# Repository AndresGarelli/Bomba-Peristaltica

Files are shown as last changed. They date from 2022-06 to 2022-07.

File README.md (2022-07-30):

English version (Spanish version at the end) updated 2022-07-30

Peristaltic pump

The Arduino code is based on https://www.thingiverse.com/thing:2619479/files and modified to meet my needs, especially related to calibration. 
We do not need to fill the vials with an exact volume, so I designed a “by eye” calibration method.

Two critical points to consider:
-	Use PETG to print rotor pieces. It resists quite well up to 85ºC. On the other hand, PLA, the most frequently used material for 3D printing softens at 65C. The rest of the pieces were printed with PLA and work fine, at least for the moment.
-	Food temperature: We cook the fly food at 95ºC for 30 minutes. That high temperature softens PLA, and probably PETG. We now cook the food at 95 and let it cool (and maintain it at) 75ºC to deliver into the vials. It is very important to keep food at a constant temperature to deliver a reproducible volume. Food viscosity increases when temperate decreases and if the pump has been calibrated at a high temperature to deliver a given volume in a given number of rotations, then the volume delivered by the same number of rotations will be smaller when the food cools down.

The design of the rotor is a modification of https://www.thingiverse.com/thing:3148717. I followed the designer recommendation to print with 100% infill. Remember to use PETG, at least for the rotor.

Two different calibration values can be saved in the programs named “moscas” (flies) and “gusanos” (worms). If necessary, those names can be changed in lines 161 and 162 of the code.

The pressure of the cover over the hose is adjusted with two long screws. If the cover is too loose, the rotor will not make enough pressure onto the hose and the food will not be pumped. If it is too tight, it will block the motor. The exact position should be found by trial and error. If you find that my design does not work in your hands, you can try with the original one https://www.thingiverse.com/thing:3148717.

A few comments on the electronic circuit. There are three things that are optional and can be removed. The first one is the possibility to activate the pump with a pedal. We found that it was not necessary after adding the option to repeat pumping cycles to the code. The second one are the three LEDs that indicate the mode of operation that is selected. The same information is shown in the screen. The last one is the fan to cool the motor and the motor driver. It does not seem necessary since none of them gets too hot during operation.

Bill of Materials (with links to suppliers in Argentina)

1- Stepper motor, 1.5A high Torque 4.2kg 17HS4401S   x1 https://articulo.mercadolibre.com.ar/MLA-899670687-nema-17-motor-paso-a-paso-18-alto-t-15a-usongshine-_JM

2- Bearings  605zz	x9	https://articulo.mercadolibre.com.ar/MLA-915854069-rodamiento-ruleman-605-zz-x20-unidades-_JM

3- driver A4899		x1 https://www.todomicro.com.ar/motores-y-drivers-motores/288-modulo-a4988-pololu-driver-motor-paso-a-paso.html

4- arduino promini 5V (it will also work with proMini 3.3V or arduino UNO)	x1

5- Power source 12V 2A		x1

6- step down regulator MP1584 	x1

7- 16x2 LCD display with I2C adapter	x1

8- Rotary encoder Ky-040 	x1

9- LEDs 3mm (optional)	x3

10-  100uF capacitor	x1

11- resistors 220 Ohm, 10kOhm

12- Fan, 6cm (optional)	x1

13- Plastic box: it can be printed, I used a 20x30 cm for electrical installations

14- silicone hose, external diameter 10mm, inner diameter 6mm (walls 2mm). 

15- nuts, bolts, screws, etc

It is critical to limit the current through the motor driver!

This is VERY important. If this is not correctly done the motor can be damaged. For a detailed explanation, visit this webpage: https://www.pololu.com/product/1182
I used a cheap driver that does not have the same resistor values as the original one. This has to be taken into account when setting the current limit.  I provide the details of the procedure for my motor and driver, you should do your own calculations:

Motor 17HS4401S

Max current 1.5A

For a A4988 driver:  Imax = Vref/8*limiting resistor.

Imax is 1.5

Resistor: R100 0.1Ohm or 100 mOhm

Vref= 1.2V

The driver is configured to work in a quarter steps  mode with a logic level of 5V.
Turn the potentiometer of the driver until you get the Vref. In my case, I had to put the potentiometer at the max max level to get a  Vref of 1.19V.

User instructions:

The LCD display shows a menu with 11 options that can be navigated turning the knob clockwise or counterclockwise. Menu options are selected by pressing the knob once. Once inside the option, turn the knob to set values and press again to leave.
If the knob is pressed continuously the motor will move at a constant speed until the knob is released. That will let the operator fill the hose with food.
The pumb has three operation modes: Dosifica (dosing), bombea (pump), calibra (calibration).

MENU OPTIONS 

0: Start--> starts the selected mode (dosifica/bombea/calibra). Pressing a second time stops the pump once the current cycle is finished.

1: Tiempo (time)--> Sets the time required to fill one vial. When this value is set, the speed expressed as RPM is automatically calculated. If the resulting speed is > 200 RPM, the time is decreased to get a max speed of 200 RPM.

2: Velocidad (speed)--> Sets the speed, expressed in RPM, and calculates the time required to fill one vial.

3: Ciclos (cycles) --> Number of filling cycles that will be executed when pressing START (number of vials to fill). Max value is 200. This value can be increased in line 139 of the code.

4: Pausa (pause) --> Resting time between two consecutive cycles.

5: Modo (mode)--> It has three options. Dosifica (= dosing. The motor will move a given number of turns defined during the calibration and stop for the time established in menú 5. The cycle is repeated the number of times indicated in menú 4). Bombea (=pump. The motor turns at a constant speed) and Calibra (=calibration. The pump executes a calibration cycle and returns to the dosing mode)

6: PGM --> Used to store two different dispensing volumes (ie two different calibration values)

7: Sentido (turning direction)--> H (Horario: clockwise) and AH (AntiHorario: counter clockwise)

8:  M--> is the number of steps that the motor will move in the program “Moscas” (200 steps is one turn. In fact, as the driver is set at quarter steps, 800 steps are required to move the motor one turn. The number set in this menu is internally multiplied by 4). 

9: G--> Same as above, but for the program Gusanos. Both 9 and 10 can be manually set, and the speed will be automatically calculated to complete the cycle in the time indicated in menu 2 (time). 

10: Saves the configuration in the memory of the Arduino board. The values of each parameter are loaded from memory at start. After calibration (or changing speed, cycles, puase time, etc) the new settings can be saved by selecting this option. 

How to use the pump?

Place the silicone hose between the rotor and hose cover and tighten the cover with the screws until an optimal position is reached. An optimal position is that at which the bearings are tightly adjusted to hose and the motor is not blocked. (https://youtu.be/28UxOIC15p4)

Calibration

Select the program to calibrate in menú 7 (Moscas or gusanos. Or, for example, big and small vial)
Select the option “calibrar” in menú 6. The LCD will show the message “Presionar hasta llenar el tubo” (press until the vial is filled).
Place the end of the hose inside one empty vial and keep the knob pressed. The motor will begin to move slowly and pump the food. Release the knob when the desired level of food is reached. The program will save the number of turns and calculate how long it will take to fill one vial (menu 2) at the speed set in menu 3. The number of turns and steps will be diplayed for a few seconds and will automatically change to the dosing mode.

Pumping

Go to menú 1 and press the knob. The motor will move and the Word RUN will be displayed in the screen. 
If the mode “bombea” is selected, the motor will rotate until the knob is pressed again.
If it is in mode “Dosifica”, the motor will move for one cycle, make a pause and repeat the process as many times as indicated by menu4. Press the knob to stop dosing. Remember that the motor will stop once the current cycle has finished.

Versión en castellano

Bomba peristáltica

El código del arduino está basado en https://www.thingiverse.com/thing:2619479/files  y modificado según mis necesidades, en particular, la forma de calibración. Nosotros no necesitamos un volumen exacto y además la consistencia de la comida varía bastante en función de la temperatura, por lo que el ajuste para que dispense un cierto volumen puede cambiar bastante en función de la temperatura de la comida. Por eso implementé un calibrado “a ojo” que es más que suficiente para mis necesidades.

Hay dos puntos críticos a tener en cuenta:
-material utilizado para imprimir las piezas: el PLA se ablanda a 65ºC aproximadamente. Las primeras pruebas fueron impresas con ese material y no funcionaron bien, en particular, el rotor. Por eso rediseñé el rotor y lo imprimí en PETG, que resiste bien hasta 85C. El resto de las piezas no fueron reimpresas en ese material. Aparentemente, funcionan bien en PLA.
-temperatura de la comida: cocinamos la comida en una olla a baño maría con termostato fijo a 95C. A esa temperatura, el PLA se ablanda. El rotor es particularmente sensible a este efecto porque se deforma el orificio donde encaja el motor. Por eso, lo reimprimimos con PETG y además bajamos la temperatura a 70C para distribuirla. Es decir, cocinamos a 95 y luego bajamos a 70C. De esa manera, logramos distribuir 4 litros de comida sin ningún inconveniente. Por otra parte, es importante que se mantenga la temperatura de la comida ya que si se calibra a una temperatura para que impulse un cierto volumen de comida en cada ciclo y luego la comida se enfría, el volumen dispensado va a ser menor. La solución es recalibrar (es muy fácil de hacer) cuando sea necesario o mantener la comida a una temperatura fija.

El modelo inicial del rotor fue copiado de https://www.thingiverse.com/thing:3148717 pero luego modificado y es el que se adjunta. Recomienda imprimirlo con infill 100%. Yo recomiendo usar PETG, al menos para el rotor.

Mi idea era hacer una bomba que pudiera usarse por dos laboratorios diferentes, el mío, que trabaja con moscas y otro de gusanos (por eso tiene dos programas denominados “moscas” y “gusanos”. Se puede cambiar el nombre en las líneas 161 y 162 del código). En este último caso, se necesita distribuir un medio de cultivo estéril y por lo tanto, necesitan esterilizar la manguera luego de cada uso. Para que fuera sencillo cambiar la manguera luego de cada uso diseñé las piezas que adjunto. Pero luego no funcionaron tal como esperaba, ya que para evitar que el motor se trabe es necesario que las piezas tengan algo de juego, que puedan moverse levemente. La solución que encontré fue hacerles un agujero con un taladro y atravesar un tornillo para mantener unidas las dos piezas entre sí y dejar que puedan moverse. Los orificios ya están incluidos en el modelo adjunto. Este diseño se parece bastante en su funcionamiento a aquel del que copié el rotor. La manguera puede aun cambiarse con relativa facilidad. Si sólo vas a ser usado para comida de moscas, quizás pueda ser más práctico imprimir directamente el modelo completo del que saqué el rotor, que también incluye una carcasa para alojar el motor y el controlador. El cambio de la manguera parece más trabajoso en ese modelo, pero eso no sería un inconveniente si no es necesario esterilizarla luego de cada uso ya que puede lavarse el interior pasando agua caliente.
Acerca del circuito eléctrico. Hay tres cosas que son opcionales. Una es la activación con un pedal. La idea era llenar los tubos de a uno activando la bomba con un pedal, pero encontramos que la alternativa de generar un programa con un número de ciclos (=tubos) y una pausa entre ellos era mejor. La otra característica opcional son los leds que indican el modo de funcionamiento. La última es el ventilador para enfriar el driver del motor y el motor mismo. Las especificaciones del driver indican que puede llegar a ser necesario refrigerarlo. Como es barato, preferí agregarlo, pero me parece que funcionaría igual de bien sin él.
 
Lista de materials con links a proveedores en Argentina
1- motor paso a paso (stepper motor) 1.5A Alto Torque 4.2kg 17HS4401S   x1 https://articulo.mercadolibre.com.ar/MLA-899670687-nema-17-motor-paso-a-paso-18-alto-t-15a-usongshine-_JM

2- ruleman 605zz	x9	https://articulo.mercadolibre.com.ar/MLA-915854069-rodamiento-ruleman-605-zz-x20-unidades-_JM
3- driver A4899		x1 https://www.todomicro.com.ar/motores-y-drivers-motores/288-modulo-a4988-pololu-driver-motor-paso-a-paso.html

4- arduino promini 5V (se puede usar también de 3.3V o un arduino UNO)	x1

5- Fuente 12V 2A	x1

6- Regulador step down MP1584 	x1

7- Display LCD 16x2 con adaptador I2C	x1

8- Encoder Rotativo Ky-040 	x1

9- LEDs 3mm (opcional)	x3

10- condensador de 100uF	x1

11- resistencias 220 Ohm, 10kOhm

12- ventilador de 6cm (opcional)	x1

13- caja plástica: se puede imprimir. Usé una caja estanca de aprox 20x30 cm

14- la manguera es de silicona diámetro ext 10mm, diámetro int 6mm (paredes 2mm). 

15- tornillos, tuercas…

AJUSTES de corriente máxima para el driver del motor

Este punto es muy importante. Hay que seguir las instrucciones que se encuentran aquí: https://www.pololu.com/product/1182
El módulo que conseguí no es el original y no tiene las resistencias que se indican en ese instructivo. De todas maneras, el método de ajuste es el mismo. A continuación, pego mis notas respecto de esto:

Motor 17HS4401S										intensidad máxima es 1.5A	

para ajustar el A4988 Imax = Vref/8*resistencia limitadora

Imax es 1.5      la resistencia es R100 0.1Ohm o 100 mOhm

Vref= 1.2V

Uso el driver en modo quarter steps con un nivel lógico de 5V.

Ajustando el potenciómetro del módulo al máximo, el máximo valor Vref alcanzado es de 1.19V, que es el Vref con el que se alcanza el Imax de 1.5 A
es decir, que quedó en el límite superior.

Funcionamiento:

Al encenderla, aparece en el display un menú con 11 opciones. Girando el control en sentido horario o antihorario se cambia de menú. Presionando la misma perilla, se entra en el menú y pueden seleccionarse opciones. Presionando nuevamente, se sale del menú.
En cualquier momento, si se mantiene presionado el selector comenzará a funcionar la bomba a una velocidad fija (no necesariamente la misma que la seleccionada en el menú 3) en forma continua hasta que se suelte. Eso permite llenar la manguera.

MENU

0: Start--> inicia el programa (dosifica/bombea/calibra). Presionando nuevamente, interrumpe la ejecución al finalizar el ciclo actual.

1: Tiempo --> permite establecer el tiempo de llenado deseado. Calcula automáticamente las RPM. Si RPM es mayor que 200, ajusta el tiempo para no sobrepasar 200.

2: Velocidad --> permite ajustar RPM, calcula automáticamente el tiempo de llenado.

3: Ciclos --> número de ciclos a repetir al presionar start. (es decir, número de tubos a llenar). Máximo 200. Se puede aumentar en la línea 139 del programa.

4: Pausa --> tiempo de espera entre dos ciclos. Permite posicionar la manguera sobre un nuevo tubo vacío

5: Modo --> Tiene tres opciones. Dosifica (ejecuta un ciclo durante el que gira el número de veces seleccionado durante la calibración y luego frena. Hace una pausa y vuelve a arrancar hasta completar el número de ciclos indicados en el menú 4). Bombea (el motor gira a la velocidad seleccionada en menú 3) y Calibra (ejecuta un ciclo de calibración y luego vuelva automáticamente a modo Dosifica)

6: PGM --> permite almacenar dos volumenes diferentes para dispensar comida

7: Sentido --> sentido de giro

8:  M--> es el número de pasos que da el motor en el programa moscas (200 pasos es una vuelta). 

9: G--> es el número de pasos que da el motor en el programa gusanos (200 pasos es una vuelta). 

10: Guarda configuración en memoria: Al iniciar el programa carga valores por defecto en la memoria. Luego de calibrar (o modificar la velocidad, ciclos, pausa) se debe ejecutar esta opción del menú para que se guarden en la memoria. En caso contrario, la vez siguiente que se encienda el equipo volverá a los valores por defecto.

Inicio

Ajustar la posición del cubrerotor para que los rulemanes ajusten perfectamente bien la manguera, pero que no bloqueen el motor. La manguera está bien ajustada cuando al soplar por un extremo no es posible hacer circular aire. (https://youtu.be/28UxOIC15p4)

Calibración

Seleccionar en el menú 7 un programa para calibrar (moscas o gusanos. O tubo grande/chico).
En menú 6 seleccionar la opción calibrar. Aparece un mensaje que dice: “Presionar hasta llenar el tubo”
Posicionar la manguera sobre un tubo vacío y mantener presionado el botón. El motor comenzará a girar lentamente. Soltar el botón cuando se alcance el nivel de comida deseado. El programa almacena el número de vueltas dado y calcula cuánto tiempo demorará en llenar el tubo (nuevo valor del menú 2) en función de la velocidad indicada en el menú 3. Luego muestra el  número de pasos y el número de vueltas del motor. Al finalizar la rutina pasa al modo dosifica automáticamente.

Dosificación

Girar la perilla hasta llegar al menú 1 y presionar el botón. Aparece la leyenda RUN. Según el modo, bombea, dosifica o calibra.
Si está en modo “Dosifica”, arranca el motor, cumple un ciclo y hace una pausa (de duración establecida en menú 5). Repite el proceso tantas veces como se haya indicado en el menú 4
La ejecución de la serie de ciclos se puede interrumpir presionando nuevamente la perilla. El efecto no es inmediato, primero tiene que terminar de ejecutar el ciclo actual y luego frena.

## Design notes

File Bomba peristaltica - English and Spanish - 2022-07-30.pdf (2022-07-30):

English version (Spanish version at the end) updated: 2022-07-30

## Peristaltic pump

The Arduino code is based on https://www.thingiverse.com/thing:2619479/files and modified to meet my needs, especially related to calibration. We do not need to fill the vials with an exact volume, so I designed a “by eye” calibration method.

Two critical points to consider:

- Use PETG to print rotor pieces. It resists quite well up to 85ºC. On the other hand, PLA, the most frequently used material for 3D printing softens at 65C. The rest of the pieces were printed with PLA and work fine, at least for the moment.
- Food temperature: We cook the fly food at 95ºC for 30 minutes. That high temperature softens PLA, and probably PETG. We now cook the food at 95 and let it cool (and maintain it at) 75ºC to deliver into the vials. It is very important to keep food at a constant temperature to deliver a reproducible volume. Food viscosity increases when temperate decreases and if the pump has been calibrated at a high temperature to deliver a given volume in a given number of rotations, then the volume delivered by the same number of rotations will be smaller when the food cools down.

The design of the rotor is a modification of https://www.thingiverse.com/thing:3148717. I followed the designer recommendation to print with 100% infill. Remember to use PETG, at least for the rotor.

Two different calibration values can be saved in the programs named “moscas” (flies) and “gusanos” (worms). If necessary, those names can be changed in lines 161 and 162 of the code.

The pressure of the cover over the hose is adjusted with two long screws. If the cover is too loose, the rotor will not make enough pressure onto the hose and the food will not be pumped. If it is too tight, it will block the motor. The exact position should be found by trial and error. If you find that my design does not work in your hands, you can try with the original one https://www.thingiverse.com/thing:3148717.

A few comments on the electronic circuit. There are three things that are optional and can be removed. The first one is the possibility to activate the pump with a pedal. We found that it was not necessary after adding the option to repeat pumping cycles to the code. The second one are the three LEDs that indicate the mode of operation that is selected. The same information is shown in the screen. The last one is the fan to cool the motor and the motor driver. It does not seem necessary since none of them gets too hot during operation.

Bill of Materials (with links to suppliers in Argentina)

1- Stepper motor, 1.5A high Torque 4.2kg 17HS4401S x1 https://articulo.mercadolibre.com.ar/MLA-899670687-nema-17-

motor-paso-a-paso-18-alto-t-15a-usongshine-_JM (https://articulo.mercadolibre.com.ar/MLA-899670687-nema-17-motor-paso-a-paso-18-alto-t-15a-usongshine-_JM)
2- | Bearings 605zz x9 | https://articulo.mercadolibre.com.ar/MLA-915854069-rodamiento-ruleman-605-zz-x20-
unidades-_JM (https://articulo.mercadolibre.com.ar/MLA-915854069-rodamiento-ruleman-605-zz-x20-unidades-_JM)
3- driver A4899 x1 https://www.todomicro.com.ar/motores-y-drivers-motores/288-modulo-a4988-pololu-driver-motor-paso-apaso.html (https://www.todomicro.com.ar/motores-y-drivers-motores/288-modulo-a4988-pololu-driver-motor-paso-a-paso.html)
4- arduino promini 5V (it will also work with proMini 3.3V or arduino UNO) x1
5- | Power source 12V 2A x1
6- | step down regulator MP1584 x1
7- | 16x2 LCD display with I2C adapter x1
8- | Rotary encoder Ky-040 x1
9- | LEDs 3mm (optional) x3

10- 100uF capacitor x1
11- resistors 220 Ohm, 10kOhm
12- Fan, 6cm (optional) x1
13- Plastic box: it can be printed, I used a 20x30 cm for electrical installations 14- silicone hose, external diameter 10mm, inner diameter 6mm (walls 2mm). 15- 15- nuts, bolts, screws, etc

It is critical to limit the current through the motor driver!

This is VERY important. If this is not correctly done the motor can be damaged. For a detailed explanation, visit this webpage: https://www.pololu.com/product/1182 I used a cheap driver that does not have the same resistor values as the original one. This has to be taken into account when setting the current limit. I provide the details of the procedure for my motor and driver, you should do your own calculations:

Motor 17HS4401S
Max current 1.5A
For a A4988 driver: Imax = Vref/8*limiting resistor. Imax is 1.5
Resistor: R100 0.1Ohm or 100 mOhm
Vref= 1.2V

The driver is configured to work in a quarter steps mode with a logic level of 5V. Turn the potentiometer of the driver until you get the Vref. In my case, I had to put the potentiometer at the max max level to get a Vref of 1.19V.

User instructions: The LCD display shows a menu with 11 options that can be navigated turning the knob clockwise or counterclockwise. Menu options are selected by pressing the knob once. Once inside the option, turn the knob to set values and press again to leave. If the knob is pressed continuously the motor will move at a constant speed until the knob is released. That will let the operator fill the hose with food. The pumb has three operation modes: Dosifica (dosing), bombea (pump), calibra (calibration).

Menu 0: Start--> starts the selected mode (dosifica/bombea/calibra). Pressing a second time stops the pump once the current cycle is finished.

Menu 1: Tiempo (time)--> Sets the time required to fill one vial. When this value is set, the speed expressed as RPM is automatically calculated. If the resulting speed is > 200 RPM, the time is decreased to get a max speed of 200 RPM.

Menu 2: Velocidad (speed)--> Sets the speed, expressed in RPM, and calculates the time required to fill one vial.

Menu 3: Ciclos (cycles) --> Number of filling cycles that will be executed when pressing START (number of vials to fill). Max value is 200. This value can be increased in line 139 of the code.

Menu 4: Pausa (pause) --> Resting time between two consecutive cycles.

Menu 5: Modo (mode)--> It has three options. Dosifica (= dosing. The motor will move a given number of turns defined during the calibration and stop for the time established in menú 5. The cycle is repeated the number of times indicated in menú 4). Bombea (=pump. The motor turns at a constant speed) and Calibra (=calibration. The pump executes a calibration cycle and returns to the dosing mode)

Menu 6: PGM --> Used to store two different dispensing volumes (ie two different calibration values)

Menu 7: Sentido (turning direction)--> H (Horario: clockwise) and AH (AntiHorario: counter clockwise)

Menu 8: M--> is the number of steps that the motor will move in the program “Moscas” (200 steps is one turn. In fact, as the driver is set at quarter steps, 800 steps are required to move the motor one turn. The number set in this menu is internally multiplied by 4).

Menu 9: G--> Same as above, but for the program Gusanos. Both 9 and 10 can be manually set, and the speed will be automatically calculated to complete the cycle in the time indicated in menu 2 (time).

Menu 10: Saves the configuration in the memory of the Arduino board. The values of each parameter are loaded from memory at start. After calibration (or changing speed, cycles, puase time, etc) the new settings can be saved by selecting this option.

How to use the pump?

Place the silicone hose between the rotor and hose cover and tighten the cover with the screws until an optimal position is reached. An optimal position is that at which the bearings are tightly adjusted to hose and the motor is not blocked. (https://youtu.be/28UxOIC15p4)

Calibration

Select the program to calibrate in menú 7 (Moscas or gusanos. Or, for example, big and small vial) Select the option “calibrar” in menú 6. The LCD will show the message “Presionar hasta llenar el tubo” (press until the vial is filled). Place the end of the hose inside one empty vial and keep the knob pressed. The motor will begin to move slowly and pump the food. Release the knob when the desired level of food is reached. The program will save the number of turns and calculate how long it will take to fill one vial (menu 2) at the speed set in menu 3. The number of turns and steps will be diplayed for a few seconds and will automatically change to the dosing mode.

Pumping

Go to menú 1 and press the knob. The motor will move and the Word RUN will be displayed in the screen. If the mode “bombea” is selected, the motor will rotate until the knob is pressed again. If it is in mode “Dosifica”, the motor will move for one cycle, make a pause and repeat the process as many times as indicated by menu4. Press the knob to stop dosing. Remember that the motor will stop once the current cycle has finished.

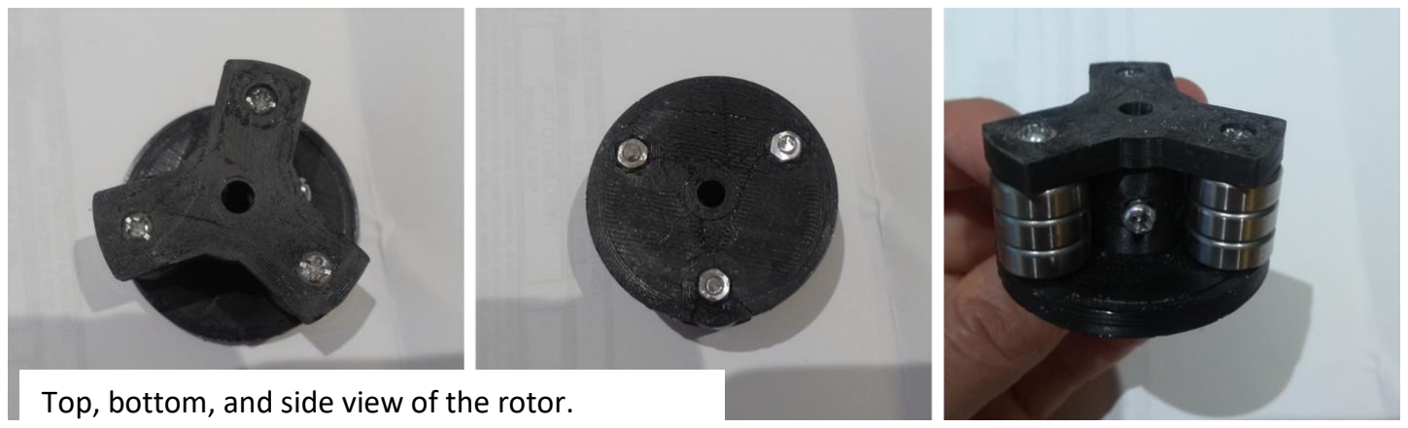
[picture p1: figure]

Top, bottom, and side view of the rotor.

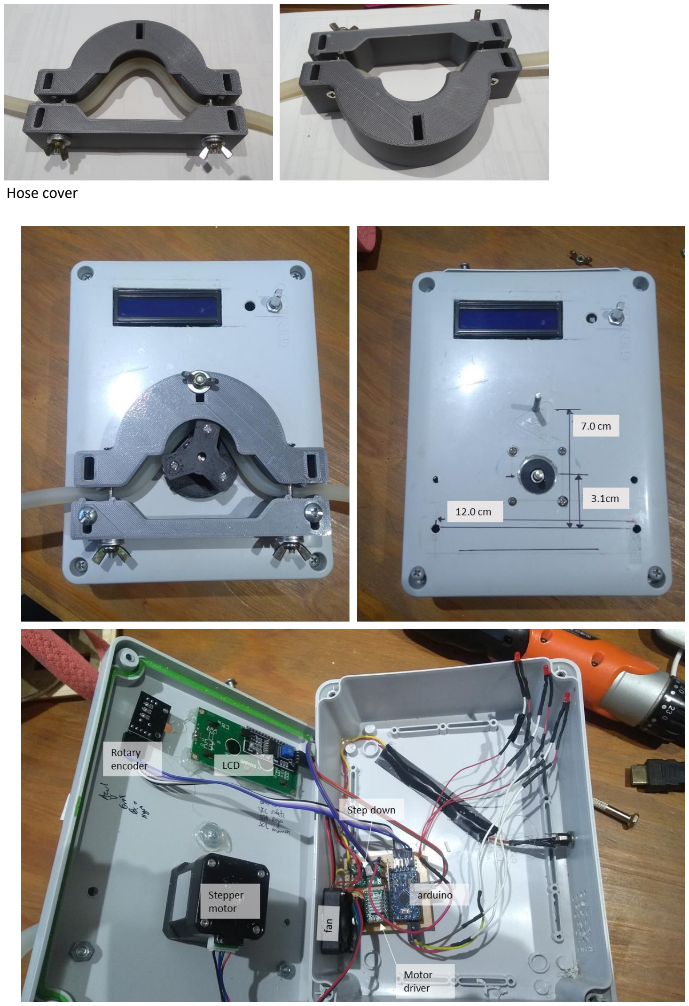
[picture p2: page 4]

Hose cover

## Versión en castellano

## Bomba peristáltica

El código del arduino está basado en https://www.thingiverse.com/thing:2619479/files y modificado según mis necesidades, en particular, la forma de calibración. Nosotros no necesitamos un volumen exacto y además la consistencia de la comida varía bastante en función de la temperatura, por lo que el ajuste para que dispense un cierto volumen puede cambiar bastante en función de la temperatura de la comida. Por eso implementé un calibrado “a ojo” que es más que suficiente para mis necesidades.

Hay dos puntos críticos a tener en cuenta: -material utilizado para imprimir las piezas: el PLA se ablanda a 65ºC aproximadamente. Las primeras pruebas fueron impresas con ese material y no funcionaron bien, en particular, el rotor. Por eso rediseñé el rotor y lo imprimí en PETG, que resiste bien hasta 85C. El resto de las piezas no fueron reimpresas en ese material. Aparentemente, funcionan bien en PLA. -temperatura de la comida: cocinamos la comida en una olla a baño maría con termostato fijo a 95C. A esa temperatura, el PLA se ablanda. El rotor es particularmente sensible a este efecto porque se deforma el orificio donde encaja el motor. Por eso, lo reimprimimos con PETG y además bajamos la temperatura a 70C para distribuirla. Es decir, cocinamos a 95 y luego bajamos a 70C. De esa manera, logramos distribuir 4 litros de comida sin ningún inconveniente. Por otra parte, es importante que se mantenga la temperatura de la comida ya que si se calibra a una temperatura para que impulse un cierto volumen de comida en cada ciclo y luego la comida se enfría, el volumen dispensado va a ser menor. La solución es recalibrar (es muy fácil de hacer) cuando sea necesario o mantener la comida a una temperatura fija.

El modelo inicial del rotor fue copiado de https://www.thingiverse.com/thing:3148717 pero luego modificado y es el que se adjunta. Recomienda imprimirlo con infill 100%. Yo recomiendo usar PETG, al menos para el rotor.

Mi idea era hacer una bomba que pudiera usarse por dos laboratorios diferentes, el mío, que trabaja con moscas y otro de gusanos (por eso tiene dos programas denominados “moscas” y “gusanos”. Se puede cambiar el nombre en las líneas 161 y 162 del código). En este último caso, se necesita distribuir un medio de cultivo estéril y por lo tanto, necesitan esterilizar la manguera luego de cada uso. Para que fuera sencillo cambiar la manguera luego de cada uso diseñé las piezas que adjunto. Pero luego no funcionaron tal como esperaba, ya que para evitar que el motor se trabe es necesario que las piezas tengan algo de juego, que puedan moverse levemente. La solución que encontré fue hacerles un agujero con un taladro y atravesar un tornillo para mantener unidas las dos piezas entre sí y dejar que puedan moverse. Los orificios ya están incluidos en el modelo adjunto. Este diseño se parece bastante en su funcionamiento a aquel del que copié el rotor. La manguera puede aun cambiarse con relativa facilidad. Si sólo vas a ser usado para comida de moscas, quizás pueda ser más práctico imprimir directamente el modelo completo del que saqué el rotor, que también incluye una carcasa para alojar el motor y el controlador. El cambio de la manguera parece más trabajoso en ese modelo, pero eso no sería un inconveniente si no es necesario esterilizarla luego de cada uso ya que puede lavarse el interior pasando agua caliente. Acerca del circuito eléctrico. Hay tres cosas que son opcionales. Una es la activación con un pedal. La idea era llenar los tubos de a uno activando la bomba con un pedal, pero encontramos que la alternativa de generar un programa con un número de ciclos (=tubos) y una pausa entre ellos era mejor. La otra característica opcional son losleds que indican el modo de funcionamiento. La última es el ventilador para enfriar el driver del motor y el motor mismo. Las especificaciones del driver indican que puede llegar a ser necesario refrigerarlo. Como es barato, preferí agregarlo, pero me parece que funcionaría igual de bien sin él.

Lista de materials con links a proveedores en Argentina

1- | motor | paso | a | paso | (stepper | motor) | 1.5A | Alto | Torque | 4.2kg | 17HS4401S
x1 https://articulo.mercadolibre.com.ar/MLA-899670687-nema-17-motor-paso-a-paso-18-alto-t-15a-usongshine-_JM (https://articulo.mercadolibre.com.ar/MLA-899670687-nema-17-motor-paso-a-paso-18-alto-t-15a-usongshine-_JM)
2- ruleman 605zz x9 https://articulo.mercadolibre.com.ar/MLA-915854069-rodamiento-ruleman-605-zz-x20-unidades-_JM (https://articulo.mercadolibre.com.ar/MLA-915854069-rodamiento-ruleman-605-zz-x20-unidades-_JM)
3- | driver | A4899 | x1 https://www.todomicro.com.ar/motores-y-drivers-motores/288-modulo-
a4988-pololu-driver-motor-paso-a-paso.html (https://www.todomicro.com.ar/motores-y-drivers-motores/288-modulo-a4988-pololu-driver-motor-paso-a-paso.html)
4- | arduino promini 5V (se puede usar también de 3.3V o un arduino UNO) x1
5- | Fuente 12V 2A x1
6- | Regulador step down MP1584 x1
7- | Display LCD 16x2 con adaptador I2C x1
8- | Encoder Rotativo Ky-040 x1
9- | LEDs 3mm (opcional) x3
10- condensador de 100uF x1
11- resistencias 220 Ohm, 10kOhm
12- ventilador de 6cm (opcional) x1
13- caja plástica: se puede imprimir. Usé una caja estanca de aprox 20x30 cm
14- la manguera es de silicona diámetro ext 10mm, diámetro int 6mm (paredes 2mm). 15- tornillos, tuercas…

AJUSTES de corriente máxima para el driver del motor

Este punto es muy importante. Hay que seguir las instrucciones que se encuentran aquí: https://www.pololu.com/product/1182 El módulo que conseguí no es el original y no tiene las resistencias que se indican en ese instructivo. De todas maneras, el método de ajuste es el mismo. A continuación, pego mis notas respecto de esto:

Motor 17HS4401S según el que lo vendió la intensidad máxima es 1.5A
para ajustar el A4988 Imax = Vref/8*resistencia limitadora
Imax es 1.5 la resistencia es R100 0.1Ohm o 100 mOhm
Vref= 1.2V
Uso el driver en modo quarter steps con un nivel lógico de 5V.

Ajustando el potenciómetro del módulo al máximo, el máximo valor Vref alcanzado es de 1.19V, que es el Vref con el que se alcanza el Imax de 1.5 A es decir, que quedó en el límite superior.

Funcionamiento

Al encenderla, aparece en el display un menú con 11 opciones. Girando el control en sentido horario o antihorario se cambia de menú. Presionando la misma perilla, se entra en el menú y pueden seleccionarse opciones. Presionando nuevamente, se sale del menú. En cualquier momento, si se mantiene presionado el selector comenzará a funcionar la bomba a una velocidad fija (no necesariamente la misma que la seleccionada en el menú 3) en forma continua hasta que se suelte. Eso permite llenar la manguera.

Menú 0: Start--> inicia el programa (dosifica/bombea/calibra). Presionando nuevamente, interrumpe la ejecución al finalizar el ciclo actual.

Menú 1: Tiempo --> permite establecer el tiempo de llenado deseado. Calcula automáticamente las RPM. Si RPM es mayor que 200, ajusta el tiempo para no sobrepasar 200.

Menú 2: Velocidad --> permite ajustar RPM, calcula automáticamente el tiempo de llenado.

Menú 3: Ciclos --> número de ciclos a repetir al presionar start. (es decir, número de tubos a llenar). Máximo 200. Se puede aumentar en la línea 139 del programa.

Menú 4: Pausa --> tiempo de espera entre dos ciclos. Permite posicionar la manguera sobre un nuevo tubo vacío

Menú 5: Modo --> Tiene tres opciones. Dosifica (ejecuta un ciclo durante el que gira el número de veces seleccionado durante la calibración y luego frena. Hace una pausa y vuelve a arrancar hasta completar el número de ciclos indicados en el menú 4). Bombea (el motor gira a la velocidad seleccionada en menú 3) y Calibra (ejecuta un ciclo de calibración y luego vuelva automáticamente a modo Dosifica)

Menú 6: PGM --> permite almacenar dos volumenes diferentes para dispensar comida

Menú 7: Sentido --> sentido de giro

Menú 8: M--> es el número de pasos que da el motor en el programa moscas (200 pasos es una vuelta).

Menú 9: G--> es el número de pasos que da el motor en el programa gusanos (200 pasos es una vuelta).

Menú 10: Guarda configuración en memoria: Al iniciar el programa carga valores por defecto en la memoria. Luego de calibrar (o modificar la velocidad, ciclos, pausa) se debe ejecutar esta opción del menú para que se guarden en la memoria. En caso contrario, la vez siguiente que se encienda el equipo volverá a los valores por defecto.

Inicio

Ajustar la posición del cubrerotor para que los rulemanes ajusten perfectamente bien la manguera, pero que no bloqueen el motor. La manguera está bien ajustada cuando al soplar por un extremo no es posible hacer circular aire. (https://youtu.be/28UxOIC15p4)

Calibración

Seleccionar en el menú 7 un programa para calibrar (moscas o gusanos. O tubo grande/chico). En menú 6 seleccionar la opción calibrar. Aparece un mensaje que dice: “Presionar hasta llenar el tubo” Posicionar la manguera sobre un tubo vacío y mantener presionado el botón. El motor comenzará a girar lentamente. Soltar el botón cuando se alcance el nivel de comida deseado. El programa almacena el número de vueltas dado y calcula cuánto tiempo demorará en llenar el tubo (nuevo valor del menú 2) en función de la velocidad indicada en el menú 3. Luego muestra el número de pasos y el número de vueltas del motor. Al finalizar la rutina pasa al modo dosifica automáticamente.

Dosificación
Girar la perilla hasta llegar al menú 1 y presionar el botón. Aparece la leyenda RUN. Según el modo, bombea, dosifica o calibra. Si está en modo “Dosifica”, arranca el motor, cumple un ciclo y hace una pausa (de duración establecida en menú 5). Repite el proceso tantas veces como se haya indicado en el menú 4 La ejecución de la serie de ciclos se puede interrumpir presionando nuevamente la perilla. El efecto no es inmediato, primero tiene que terminar de ejecutar el ciclo actual y luego frena.

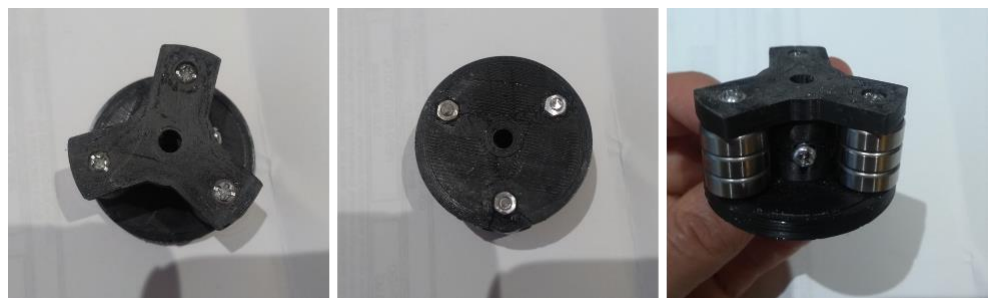
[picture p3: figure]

Vista superior, inferior y lateral del rotor

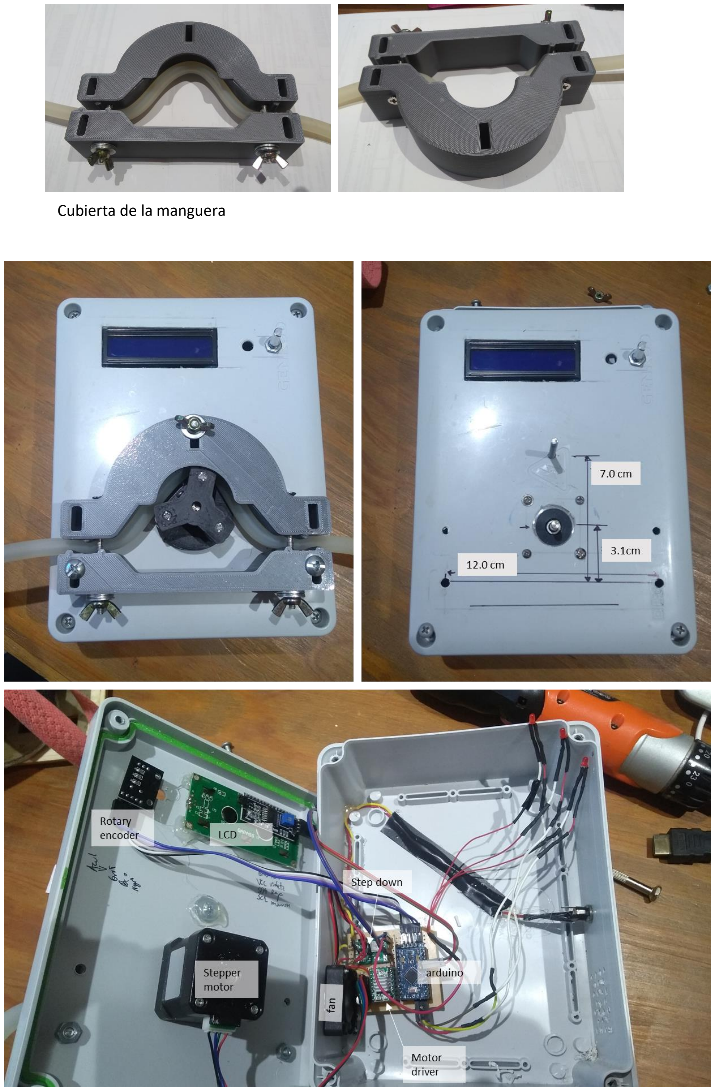
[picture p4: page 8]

Cubierta de la manguera

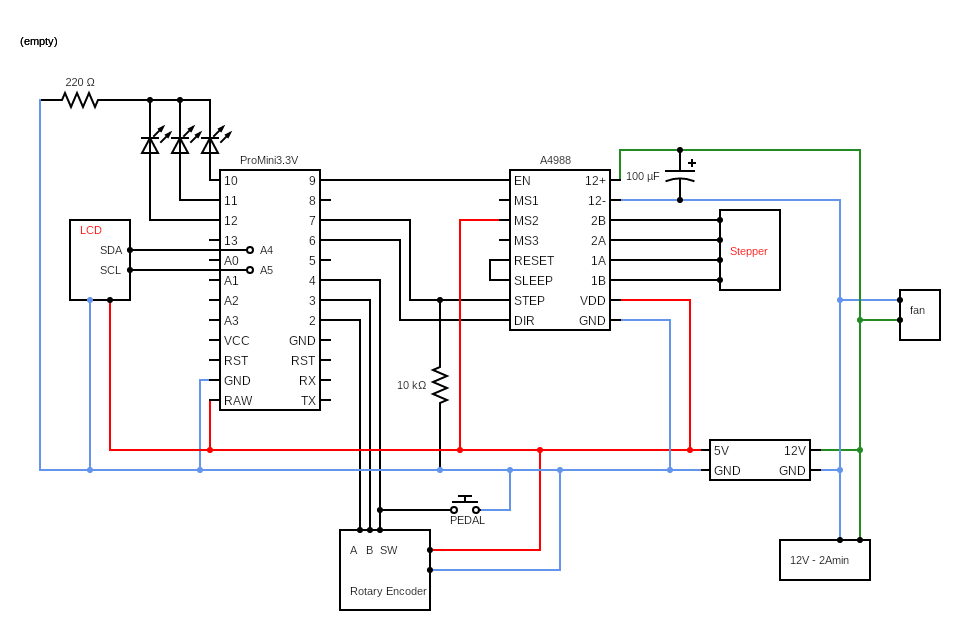
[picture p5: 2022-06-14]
bomba-B.png

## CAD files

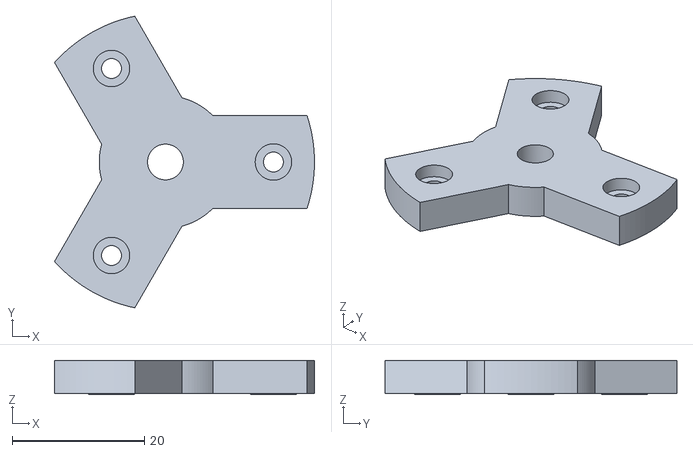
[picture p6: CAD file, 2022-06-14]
3D/Rotor-A.stl
39.3 x 44.0 x 5.20

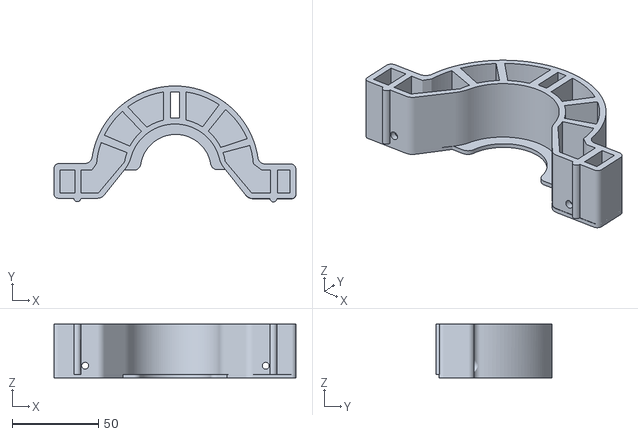
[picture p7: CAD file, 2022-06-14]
3D/piezasCubreRotor-modificado-superior.stl
140.0 x 67.1 x 31.0

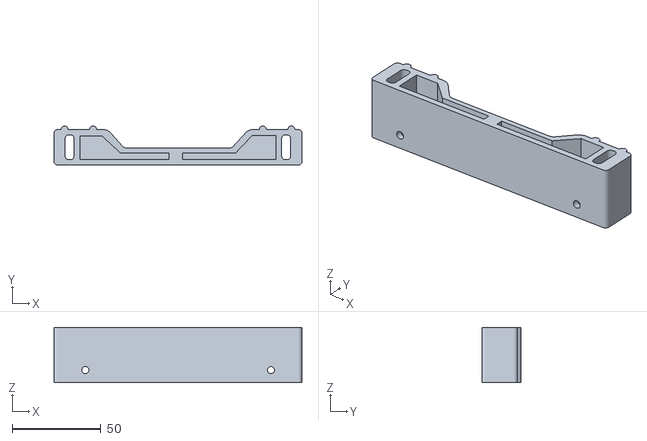
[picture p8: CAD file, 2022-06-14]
3D/piezasCubreRotor-modificado-inferior.stl
139.6 x 22.0 x 31.0

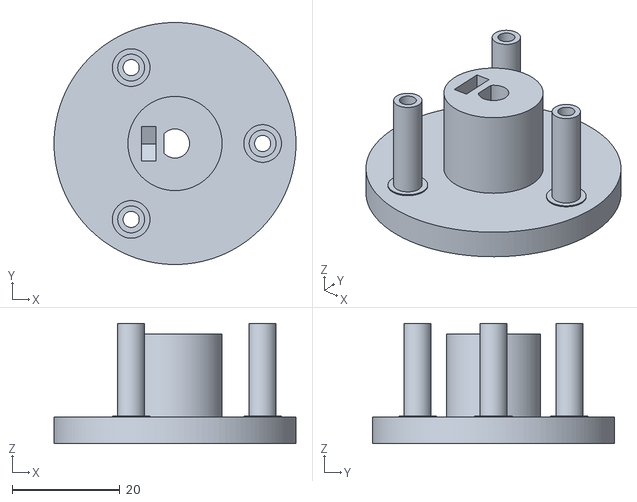
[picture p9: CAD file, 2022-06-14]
3D/Rotor-B.stl
45.0 x 45.0 x 22.4

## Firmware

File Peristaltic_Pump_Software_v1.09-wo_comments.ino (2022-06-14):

char vers[] = "1.0.9";

// include the library code:
//#include <LiquidCrystal.h> //https://www.arduino.cc/en/Reference/LiquidCrystal -> LCD control
#include <ClickEncoder.h> //https://github.com/0xPIT/encoder/blob/master/README.md -> Encoder processing (timer based)
#include <TimerOne.h> //required for ClickEncoder.h 
#include <EEPROM.h> //write and read EEPROM (to save and load settings)
#include <LiquidCrystal_I2C.h>  //https://github.com/johnrickman/LiquidCrystal_I2C
#include <Wire.h>
//LCD -----------------------------------------------------------------------------------

LiquidCrystal_I2C lcd(0x27, 16, 2);

#define LCD_COLUMNS 16
#define LCD_ROWS 2
// initialize the library with the numbers of the interface pins
//LiquidCrystal lcd(LCD_PIN_RS, LCD_PIN_EN, LCD_PIN_D4, LCD_PIN_D5, LCD_PIN_D6, LCD_PIN_D7);

//ENCODER --------------------------------------------------------------------------------
#define ENCODER_PIN_BUTTON 4
#define ENCODER_PIN_A 3
#define ENCODER_PIN_B 2
ClickEncoder *encoder;
int16_t last, value;

//STEP MOTOR -----------------------------------------------------------------------------
#define MOTOR_ENABLE_PIN 9
#define MOTOR_STEP_PIN 7
#define MOTOR_DIR_PIN 6
#define STEP_MODE 4 // (1: Full Step, 2: Half Step, 4: Quarter Step, ...)
#define STEPS_PER_FULL_ROT 200 // @ full steps
long delay_us;
long steps;
long step_counter = 0;
unsigned long pausa;


//LED indicador----------------------
const int LEDdosifica = 10;
const int LEDbombea = 11;
const int LEDcalibra = 12;



//SERIAL COMMUNICATION ---------------------------------------------------------------------
#define BAUD 9600

//STATE ------------------------------------------------------------------------------------
boolean in_menu = 0;
volatile boolean in_action = 0;
boolean menu_entered = 0;
boolean menu_left = 0;

//GENERAL -----------------------------------------------------------------------------------
#define MICROSEC_PER_SEC 1000000

//MENU ---------------------------------------------------------------------------------------
#define MAX_NUM_OF_OPTIONS 4
#define NUM_OF_MENU_ITEMS 11
#define VALUE_MAX_DIGITS 4
#define VALUE_MAX_RPM 200

int menu_number_1 = 0;
int menu_number_2 = 1;
boolean val_change = 0;
double value_dbl;
char value_str[VALUE_MAX_DIGITS + 1];


enum menu_type {
  VALUE,
  OPTION,
  ACTION
};

typedef struct
{
  const char* name_;
  menu_type type; //0: value type, 1:option type, 2:action type
  int value;
  int decimals;
  int lim;
  const char* options[4];
  const char* suffix;
} menu_item;
int menu_items_limit = 11 - 1;
menu_item menu[11];

int ciclo = 1;
bool noGota = true;
bool inwhile = false;
bool accel = true;

//███ SETUP ████████████████████████████████████████████████████████████████████████████████████████████████████
void setup() {
  // Inicializar el LCD
  Wire.begin(); //inicia biblioteca wire, asigna SDA a pin0 (D3) y SCL a pin 5 (D1);
  lcd.init();
  lcd.backlight();
  pinMode(MOTOR_STEP_PIN, OUTPUT);
  pinMode(MOTOR_DIR_PIN, OUTPUT);
  pinMode(MOTOR_ENABLE_PIN, OUTPUT);
  digitalWrite(MOTOR_DIR_PIN, LOW);
  digitalWrite(MOTOR_STEP_PIN, LOW);
  digitalWrite(MOTOR_ENABLE_PIN, HIGH);

  pinMode(LEDdosifica, OUTPUT);
  pinMode(LEDbombea, OUTPUT);
  pinMode(LEDcalibra, OUTPUT);
  digitalWrite(LEDdosifica, LOW);
  digitalWrite(LEDbombea, LOW);
  digitalWrite(LEDcalibra, LOW);


  menu[0].name_ = "Start ";
  menu[0].type = ACTION;
  menu[0].value = 0;
  menu[0].lim = 0;
  menu[0].suffix = " RUN";

  menu[1].name_ = "Tiempo: ";
  menu[1].type = VALUE;
  menu[1].value = 50;
  menu[1].decimals = 1;
  menu[1].lim = 600;
  menu[1].suffix = "s";

  menu[2].name_ = "Vel: ";
  menu[2].type = VALUE;
  menu[2].value = 60;
  menu[2].decimals = 0;
  menu[2].lim = VALUE_MAX_RPM;
  menu[2].suffix = "RPM";

  menu[3].name_ = "Ciclos: ";
  menu[3].type = VALUE;
  menu[3].value = 2;
  menu[3].decimals = 0;
  menu[3].lim = 200;
  menu[3].suffix = "";

  menu[4].name_ = "Pausa: ";
  menu[4].type = VALUE;
  menu[4].value = 15;
  menu[4].decimals = 1;
  menu[4].lim = 300;
  menu[4].suffix = "s";

  menu[5].name_ = "Modo: ";
  menu[5].type = OPTION;
  menu[5].value = 0;
  menu[5].lim = 3 - 1;
  menu[5].options[0] = "Dosifica";
  menu[5].options[1] = "Bombea";
  menu[5].options[2] = "Calibra";

  menu[6].name_ = "PGM: ";
  menu[6].type = OPTION;
  menu[6].value = 0;
  menu[6].lim = 2 - 1;
  menu[6].options[0] = "Moscas";
  menu[6].options[1] = "Gusanos";

  menu[7].name_ = "Sentido: ";
  menu[7].type = OPTION;
  menu[7].value = 0;
  menu[7].lim = 2 - 1;
  menu[7].options[0] = "H";
  menu[7].options[1] = "AH";

  menu[8].name_ = "M ";
  menu[8].type = VALUE;
  menu[8].value = 4000;
  menu[8].decimals = 0;
  menu[8].lim = 1000000;
  menu[8].suffix = " pasos";

  menu[9].name_ = "G ";
  menu[9].type = VALUE;
  menu[9].value = 4000;
  menu[9].decimals = 0;
  menu[9].lim = 1000000;
  menu[9].suffix = " pasos";

  menu[10].name_ = "Guardar Conf.";
  menu[10].type = ACTION;
  menu[10].value = 0;
  menu[10].lim = 0;
  menu[10].suffix = "OK!";

  for (int i = 0; i <= menu_items_limit; i++) {
    menu[i].value = eepromReadInt(i * 2);
  }

  encoder = new ClickEncoder(ENCODER_PIN_B, ENCODER_PIN_A, ENCODER_PIN_BUTTON, 4); //(Encoder A, Encoder B, PushButton)
  encoder->setAccelerationEnabled(false);
  Timer1.initialize(1000);
  Timer1.attachInterrupt(timerIsr);
  last = 0;

  //  Serial.begin(BAUD);

  // Print a message to the LCD.
  lcd.print("BR - ");
  //  lcd.setCursor(0, 1);
  lcd.print(vers);
  //  lcd.print(__DATE__);
  digitalWrite(LEDdosifica, HIGH);
  digitalWrite(LEDbombea, HIGH);
  digitalWrite(LEDcalibra, HIGH);
  delay(1000);
  digitalWrite(LEDdosifica, LOW);
  digitalWrite(LEDbombea, LOW);
  digitalWrite(LEDcalibra, LOW);


  //  ajusta las RPM en función del tiempo establecido en menu1 y la opcion de programa
  //menu[2].value = timeToRPM();
  menu[1].value = rpmToTIME();
  led();
  update_lcd();

  if (menu[7].value == 0) {
    digitalWrite(MOTOR_DIR_PIN, LOW);
  } else {
    digitalWrite(MOTOR_DIR_PIN, HIGH);
  }
  steps = steps_calc(menu[6].value, menu[8].value, menu[9].value);
  delay_us = delay_us_calc(menu[2].value);

}

//███ LOOP ████████████████████████████████████████████████████████████████████████████████████████████████████

void loop() {

  // BUTTON HANDLING ////////////////////////////////////////////////////////////////////////////////

  ClickEncoder::Button b = encoder->getButton();
  if (b != ClickEncoder::Open) {
    switch (b) {
      case ClickEncoder::Clicked:
        if (menu[menu_number_1].type == VALUE || menu[menu_number_1].type == OPTION) { // if value or option type
          in_menu = !in_menu;
        }
        if (menu[menu_number_1].type == ACTION) { // if action type
          in_action = !in_action;
          step_counter = 0;
          ciclo = 1;
        }

        if (in_action == true || in_menu == true) { //menu entered
          menu_entered = true;
        }

        if (in_action == false && in_menu == false) { //menu left
          menu_left = true;
        }
        if (in_action == false) {
          digitalWrite(MOTOR_ENABLE_PIN, HIGH);
          noGota = true;
          accel = true;
        }
        break;

      case ClickEncoder::DoubleClicked:
        if (menu[menu_number_1].type == VALUE) {
          menu[menu_number_1].value = menu[menu_number_1].value + menu[menu_number_1].lim / 10;
          if (menu[menu_number_1].value > menu[menu_number_1].lim)(menu[menu_number_1].value = 0);
          val_change = true;
          menu_left = true;
        }
        break;
      case ClickEncoder::Held:  //va a bombear. la idea es que se llene la manguera
        digitalWrite(MOTOR_ENABLE_PIN, LOW);
        if (accel == true) {
          acelerar(delay_us);
          accel = false;
        } else {
          pump(delay_us);
        }
        break;

      case ClickEncoder::Released:
        digitalWrite(MOTOR_ENABLE_PIN, HIGH);
        accel = true;
        break;
    }
  }


  /// SETUP ////////////////////////////////////////////////////////////////////////////////

  if (menu_entered) {
    lcd.blink();
    if (menu[menu_number_1].type == ACTION) {
      if (menu_number_1 == 0 && menu[5].value == 0) {
        lcd.setCursor((strlen(menu[menu_number_1].name_) + 2), 0);
        lcd.print(ciclo);
        lcd.print("/");
        lcd.print(menu[3].value);
        lcd.print("     ");
      } else {
        lcd.setCursor((LCD_COLUMNS - strlen(menu[menu_number_1].suffix)), 0);
        lcd.print(menu[menu_number_1].suffix);
        lcd.setCursor(15, 0);
      }
    }
    if (menu[menu_number_1].type == VALUE) {
      encoder->setAccelerationEnabled(true);
    }
    menu_entered = false;
  }



  /// ACTIONS ////////////////////////////////////////////////////////////////////////////////

  if (in_action) {
    switch (menu_number_1) {
      case 0: //Start

        if (menu[5].value == 0) { //Dose
          if (dose(steps, delay_us, step_counter, menu[3].value)) {
            exit_action_menu();
          }
        } else if (menu[5].value == 1) {      //Pump
          digitalWrite(MOTOR_ENABLE_PIN, LOW);
          if (accel == true) {
            acelerar(delay_us);
            accel = false;
          } else {
            pump(delay_us);
          }

        } else if (menu[5].value == 2) {      //Cal.
          if (calibrarMoscasGusanos()) {
            exit_action_menu();
          }
        }
        break;

      case 10:
        for (int i = 0; i <= menu_items_limit; i++) {
          eepromWriteInt(i * 2, menu[i].value);
        }
        delay(700);
        menu_left = true;
        break;
    }

    /// MENU (no action) ////////////////////////////////////////////////////////////////////////////////

  } else if (!in_action) {
    digitalWrite(MOTOR_ENABLE_PIN, HIGH);
    if (val_change == true) {
      update_lcd();
      val_change == false;
    }

    value += encoder->getValue(); // encoder update

    if (!in_menu) { // no menu selected
      val_change = encoder_selection(menu_number_1, menu_number_2, menu_items_limit); //process value change. cambia menu

    } else if (in_menu) { // menu selected
      if (menu[menu_number_1].type == 0) {
        val_change = encoder_value_selection(menu[menu_number_1].value, menu[menu_number_1].lim);
      } else {
        val_change = encoder_selection(menu[menu_number_1].value, menu[menu_number_1].lim); //////////////////////////////
        ///////////////////////////////////////////////////////////////////////////hay dos funciones encoder selection. no habrá que cambiarles el nombre? NO--> se elige la función según el número de parámetros
      }
    }

  }

  /// CLOSE ////////////////////////////////////////////////////////////////////////////////

  if (menu_left) {
    lcd.noBlink();
    if (menu[menu_number_1].type == ACTION) {
      exit_action_menu();
    }
    if (menu[menu_number_1].type == VALUE) {
      encoder->setAccelerationEnabled(false);
    }

    if (menu_number_1 == 1) {  //tiempo
      menu[2].value = timeToRPM();
    }

    if (menu_number_1 == 2) {    //velocidad
      menu[1].value = rpmToTIME();
    }

    if (menu_number_1 == 5) {    //modo
      menu[1].value = rpmToTIME();
      led();
    }

    if (menu_number_1 == 6) {    //PGM
      menu[1].value = rpmToTIME();

    }
    if (menu_number_1 == 7) { //Change Direction
      if (menu[7].value == 0) {
        digitalWrite(MOTOR_DIR_PIN, LOW);
      } else {
        digitalWrite(MOTOR_DIR_PIN, HIGH);
      }
    }

    if (menu_number_1 == 8 || menu_number_1 == 9) {    //pasos
      menu[1].value = rpmToTIME();
    }

    steps = steps_calc(menu[6].value, menu[8].value, menu[9].value);
    delay_us = delay_us_calc(menu[2].value);
    update_lcd();
    menu_left = false;
  }

}

//███ FUNCTION DECLARATION █████████████████████████████████████████████████████████████████████████████████████████████████

//_____________________________________________________________________________________________
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
